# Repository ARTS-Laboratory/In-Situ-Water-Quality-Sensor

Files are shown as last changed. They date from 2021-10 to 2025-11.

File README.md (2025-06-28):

# In-Situ-Water-Quality-Sensor
An in situ water quality sensor for monitoring water quality from a UAV-deployable sensor package. The sensor packages provide real-time monitoring of pH, conductivity, temperature, and turbidity. 

<p align="center">
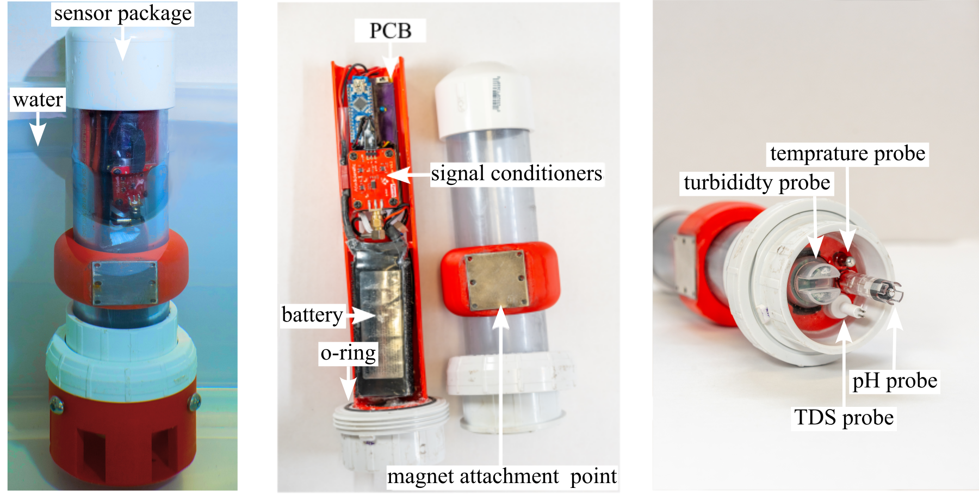
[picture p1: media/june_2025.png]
 <br> 
UAV deployment mechanism as of June 2025.
</p>

<p align="center">
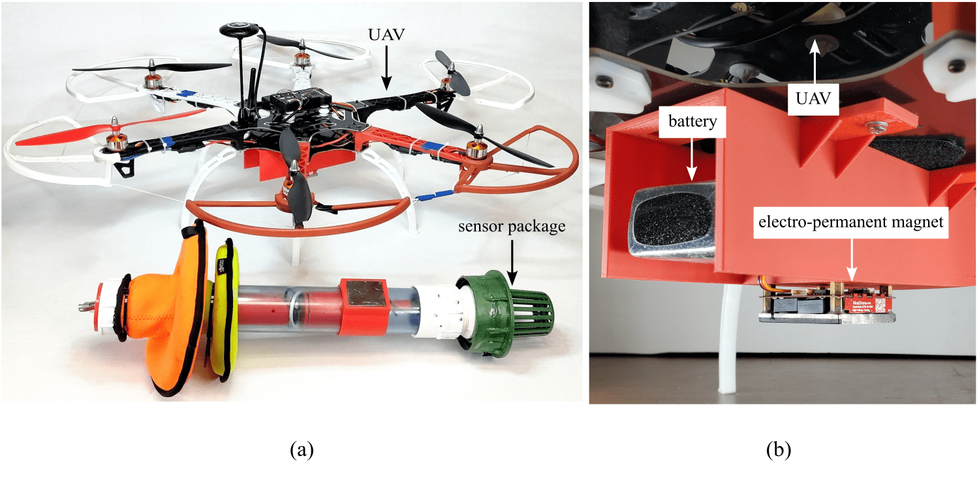
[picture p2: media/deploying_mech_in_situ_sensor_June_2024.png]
 <br> 
UAV deployment mechanism as of June 2024.
</p>

<p align="center">
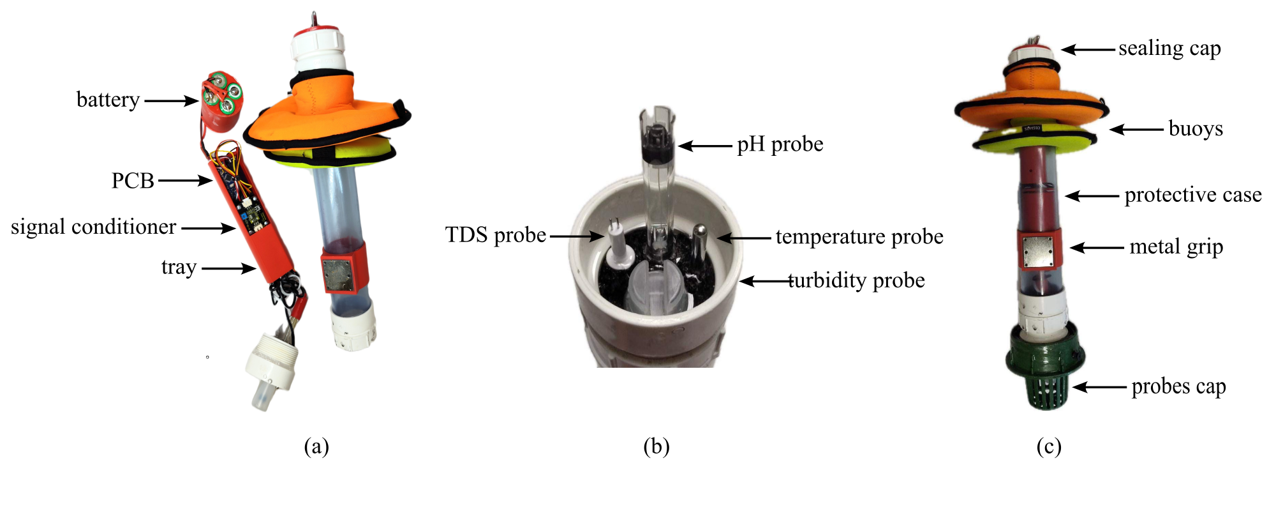
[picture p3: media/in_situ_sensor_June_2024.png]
 <br> 
System configuration as of June 2024 used for testing UAV deployments. 
</p>

<p align="center">
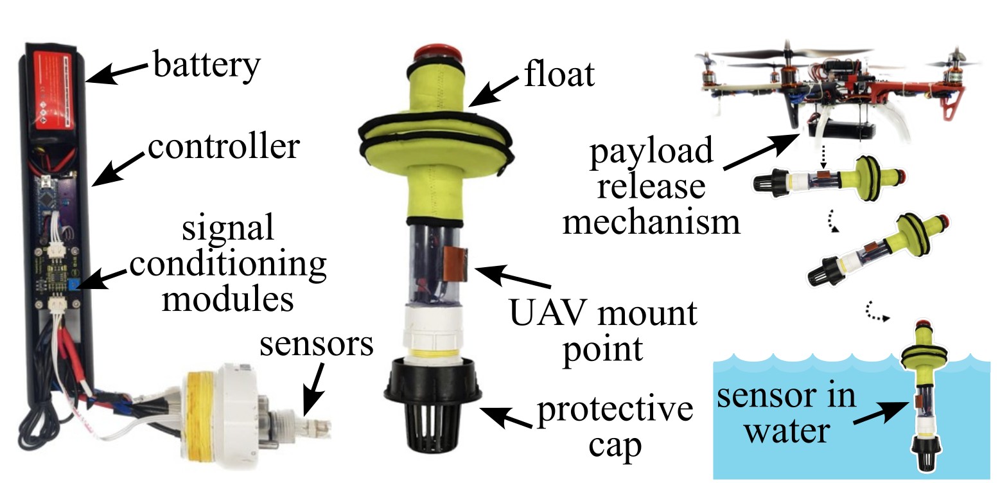
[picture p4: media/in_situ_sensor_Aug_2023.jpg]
 <br> 
System configuration as of August 2023 used for testing UAV deployments. 
</p>

<p align="center">
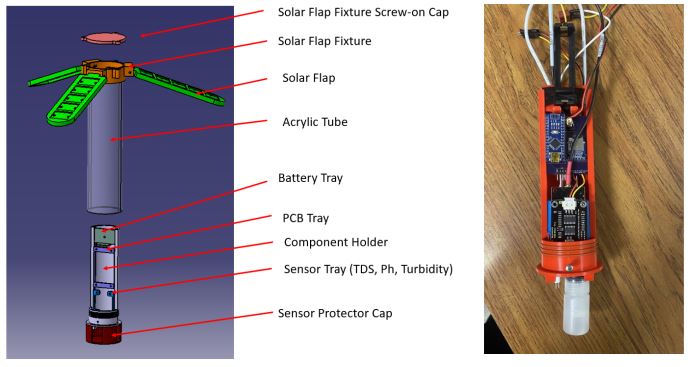
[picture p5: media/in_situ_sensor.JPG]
 <br> 
An early configuration of the proposed UAV-deployable in situ water quality system with pedal-style solar panels. 
</p>

## [System Design](system_design)
The system (hardware and software) design for the project.

## Licensing and Citation

This work is licensed under a Creative Commons Attribution-ShareAlike 4.0 International License [cc-by-sa 4.0].



Cite this data as: 

#### Bibtex

@Misc{ARTSLabSituWaterQuality,    
  author = {{ARTS-L}ab},  
  howpublished = {GitHub},  
  title  = {In-Situ-Water-Quality-Sensor},  
  groups = {ARTS-Lab},    
  url    = {https://github.com/ARTS-Laboratory/In-Situ-Water-Quality-Sensor},   
}

<p align="center">
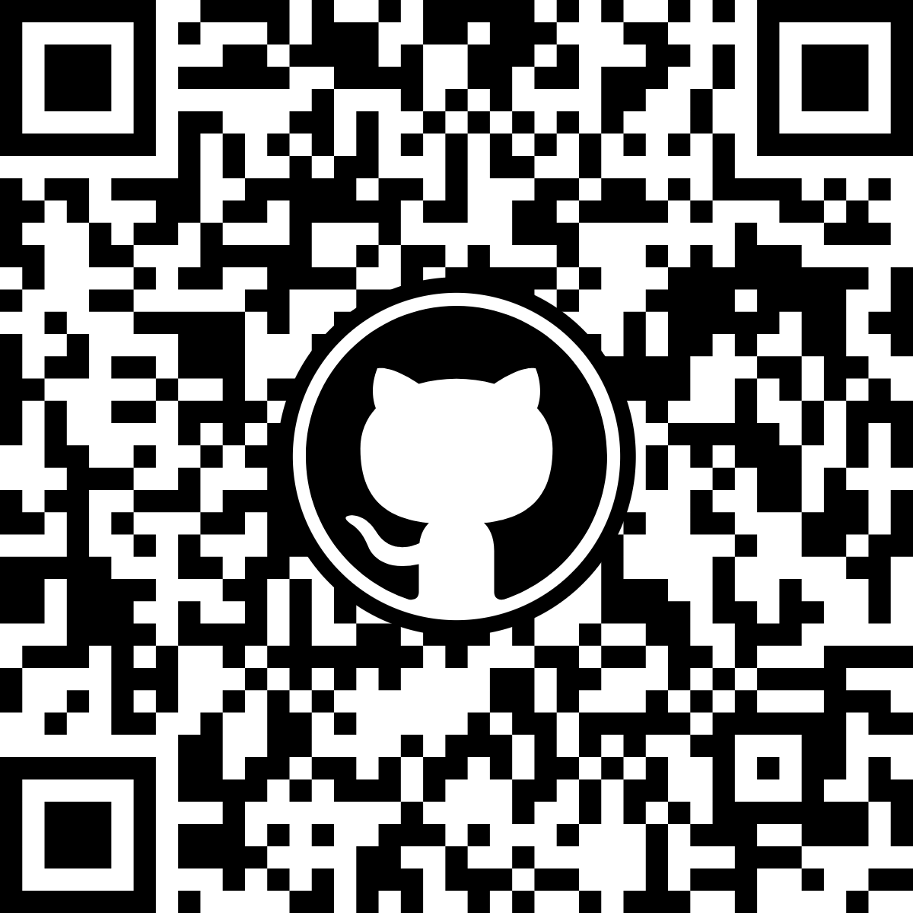
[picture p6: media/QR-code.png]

</p>
<p align="center">
QR code for repo.

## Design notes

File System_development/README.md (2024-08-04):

# Sensor Package Variations  
Sensor package variations are named after freshwater lakes in South Carolina. 

## Jocassee
* Sensor package designed for data acquisition with onboard data storage and wireless data transmission. 

## Marion 
* Sensor package designed with edge AI capabilities.

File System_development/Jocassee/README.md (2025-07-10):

# Jocassee
An in situ water quality sensor for monitoring water quality

## V0.1
1. Measures pH and turbidity 
1. Saves data to SD card
1. Water-tight case 
1. This is a general dump of all the initial files. 

## V0.2
1. This is just a clean-up version of 0.1. 
1. The pads on the 1026 resistors are too small
1. move the SMA connection over.
1. Need to add a ground plane to V0.3.
1. Need to add the SMA footprint on V0.3.

## V0.3
1. New designs for PCB boards. 

## V 0.4.0
1. Includes part designs necessary to assemble the water sensor package.
2. Missing probe protector.
3. Missing Apple air tag mount.
4. Need to adjust hold positioning for Solar Flap Fixture.

## V 0.4.5 
1. Includes 2 component holders. One for TDS and pH, and another for TDS, pH, and Turbidity.
2. Includes a probe protector that prevents damage to the ends of the probes.
3. Updated solar flaps to house solar flaps wired in parallel
4. Solar Flap Fixture Cap updated to include a spot for Apple air tag
5. Updated Solar Flap Fixture. (position for holes moved, height extended, and inside tabs reduced from 4 to 2)
6. Need to make these parts out of solid plastic pieces and leak-test the package.
7. PCB Design includes RTC Module and Micro SD Card Module.
8. The PCB includes Footprints for the PH, TDS, and Turbidity Sensors.
9. Updated Arduino code to Measure the PH, TDS, and Turbidity of the water.
10. The code controls the sampling time and saves the collected data on a micro SD card.

## V 0.4.6 
1. These are general updates and a major reorganization of all the files in V0.4.5.
2. The updated PCB design includes footprints pH, Turbidity, TDS, and Temperature sensors.
3. The Updated Arduino code.
4. The Kriging Code

## V 0.4.7
1. The updated PCB design includes footprints for a GPS Module
2. Updated Arduino Code to include GPS readings
3. Added multiple designs for 3D printed Buoys
5. Added a design for a cap that includes a spot to attach an antenna
6. Included STL files and G-code for each buoy and cap.
7. Added an assembly to better size 3D printed parts for the Chassis
8. Added a Bill of Matirials

## V 0.5.0
### Version of Refrence for "UAV-Deployable Sensor Nodes for Spatial and Temporal In-Situ Water Quality Monitoring and Mapping", Burnett et al. 2025
 1. Minor changes to chassis to more densly pack the sensors
 2. Minor Buoy/drop mechanism design revisions
 3. Minor changes to PCB mounting screw holes
sensor_package_2025

## V 0.5.1
### Usability upgrades on V 0.5.0
    
## V 0.6.0
1. Updated PCB design including GPS, wireless module and latest compact signal conditioning boards for pH & TDS sensing.
2. Includes an easily dettachable solar buoy for increased operational endurance.
3. Includes waterproof connector for solar power input and battery charging from external sources.
4. Contains a BMS for effecient battery charging and load sharing.
5. Features a capless design where O'ring is used to seal the top opening.
6. Includes step files for every components used in sensor node.

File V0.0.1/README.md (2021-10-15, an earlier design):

# V1

## Case design
1. Three o-rings
1. 3D printed end caps
1. PCV case
1. Solar Wing
1. Turbidity Case
1. Solar Connection

## PCB Design
1. pH sensor on mezzanine board 
1. Real-time clock on PCB
1. MicroSD adaptor for data collection
1. Battery slot for powering the PCB
1. CR1025 battery for Real-time clock
1. Rails for connecting to the turbidty PCB

## Code
1. Records data
1. Calibration done on the micro-controller.

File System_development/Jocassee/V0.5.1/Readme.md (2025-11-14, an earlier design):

## Instructions for the In-Situ Water Quality Sensor Deployment and Recovery <br>

### Deployment- <br>

* Upload the code and monitor the sensor readings. 

* Insert the SD card. 

* Rename the CSV file according to the sensor package number within the arduino IDE. 

* Turn the switch off. 

* Install the battery. 

* Turn the switch on. 

* Check the red signal on the board. 

* Assemble the outer case and the sensor package, put grease on the O-ring. 

* Remove the pH probe cover Tape the inside of the bottom protective red cover. 

* Mount the bottom cover. 

### Recovery- 

* Rinse the entire sensor package with tap water and wipe it dry. 

* Remove the bottom cover. 

* Rinse the sensor probes with filtered or distilled water, sepcially the pH probe. 

* Separate the outer case from the sensor package. 

* Turn the switch off. 

* Reattach the storage solution tube to the pH probe and store it properly. 

* Remove the battery. 

* Remove the SD card. 

* Check the recorded data. 

### Note: pH probe storage solution needs to be changed every 2 storage cycles.

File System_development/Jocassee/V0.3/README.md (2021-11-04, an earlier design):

# V1

## Case design
1. Three o-rings
1. 3D printed end caps
1. PCV case
1. Solar Wing
1. Turbidity Case
1. Solar Connection

## PCB Design
1. pH sensor reverse engineered onto mezzanine board
1. Real-time clock on PCB
1. MicroSD adapter for data collection
1. Battery slot for powering the PCB
1. CR1025 battery for Real-time clock
1. Rails for connecting to the turbidity PCB

## Code
1. Records data
1. Calibration done on the micro-controller.

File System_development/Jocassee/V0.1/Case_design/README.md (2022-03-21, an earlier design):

# Case Design

## file #1
1. ...

## file #2
1. ...

## file #3
1. ...

## file #4
1. ...

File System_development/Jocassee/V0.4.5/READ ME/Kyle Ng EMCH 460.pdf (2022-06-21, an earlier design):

# WATER SENSOR PACKAGE

## Kyle Ng

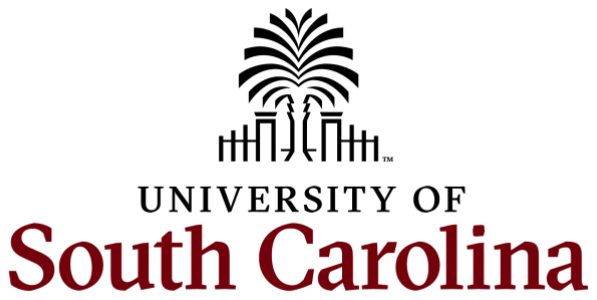
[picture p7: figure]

# PLAN FOR ENVIRONMENTAL SENSOR PACKAGE

## 1. Create a datalogger for TDS sensor 2. Combine all the sensors into one datalogger 3. Design PCB to tie everything together 4. Design waterproof case to house all components 5. Test and validate

1/18/2022

## - Need to order TDS Probe and obtain a SD card and SD card reader - RTC, SD card reader, and TDS sensor code

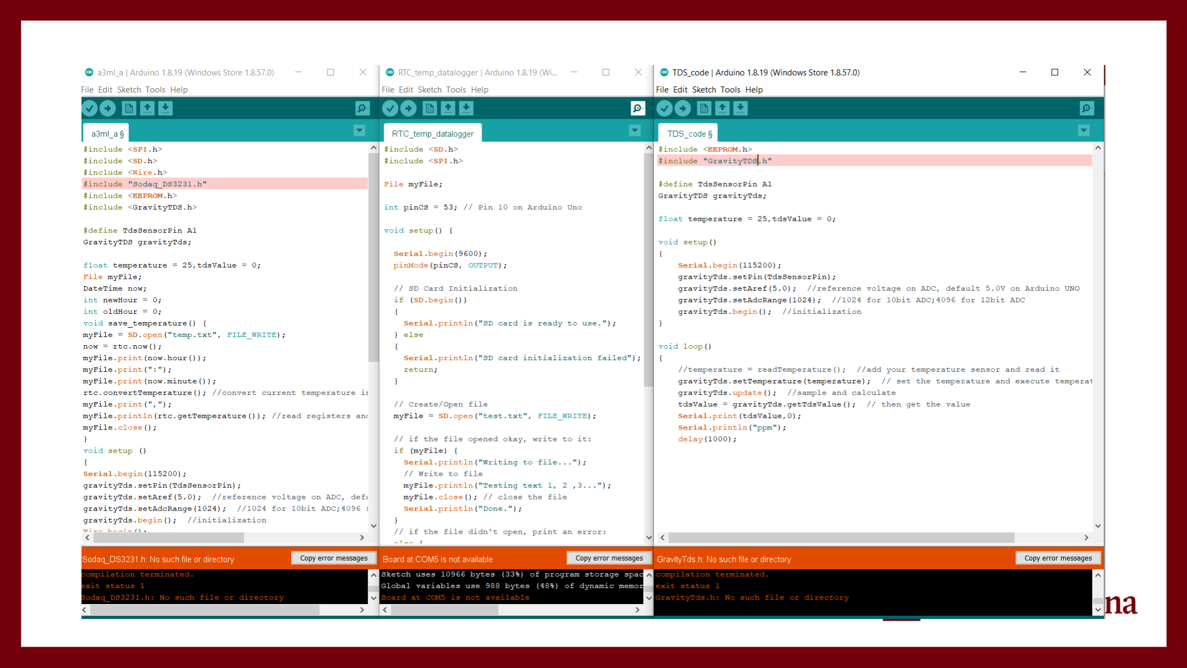
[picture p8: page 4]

1/25/2022

## - Code for TDS sensor data logging to SD card working - Need to test code when probe arrives

2/1/2022

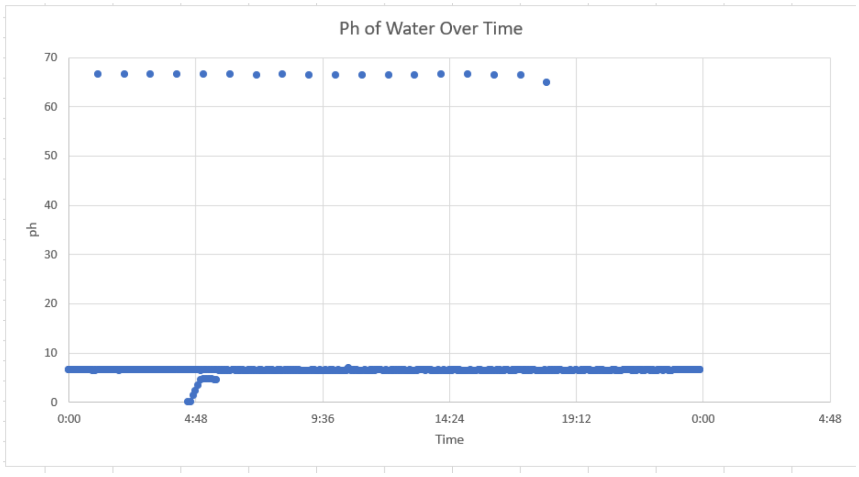
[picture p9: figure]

## Turbidity

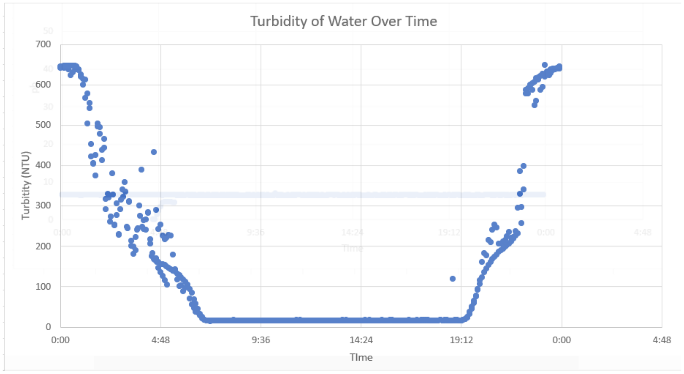
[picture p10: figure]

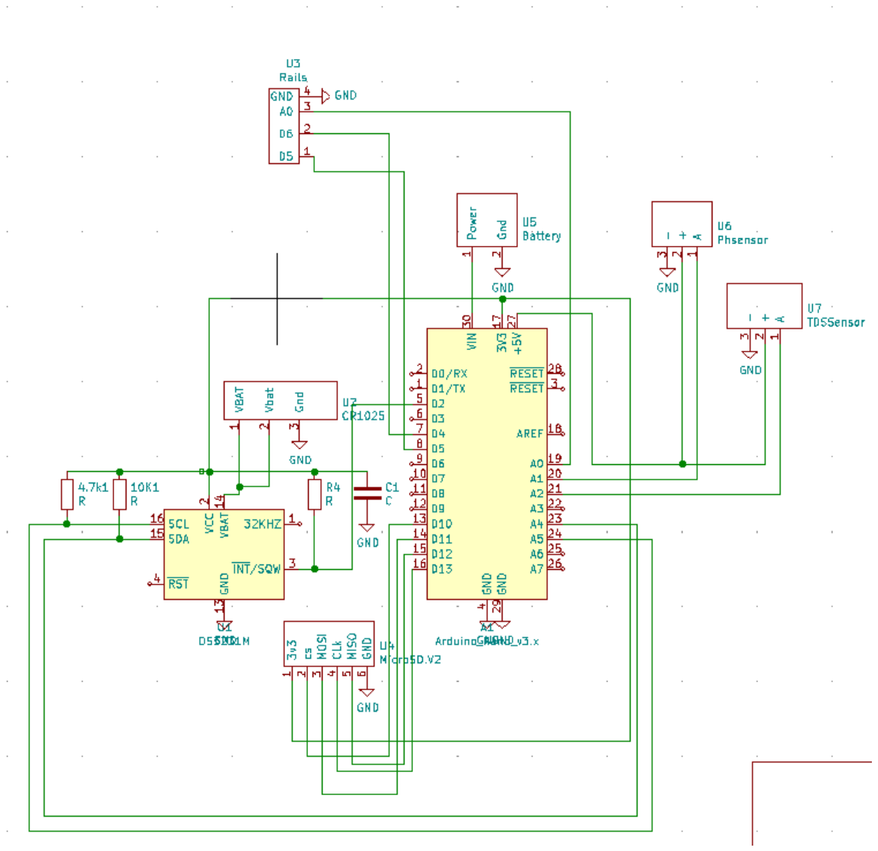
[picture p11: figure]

2/15/2022

- Included TDS sensor into current sensor package
- Next Step: rearrange
components on board to fit in new housing

# HOUSING FOR SENSORS

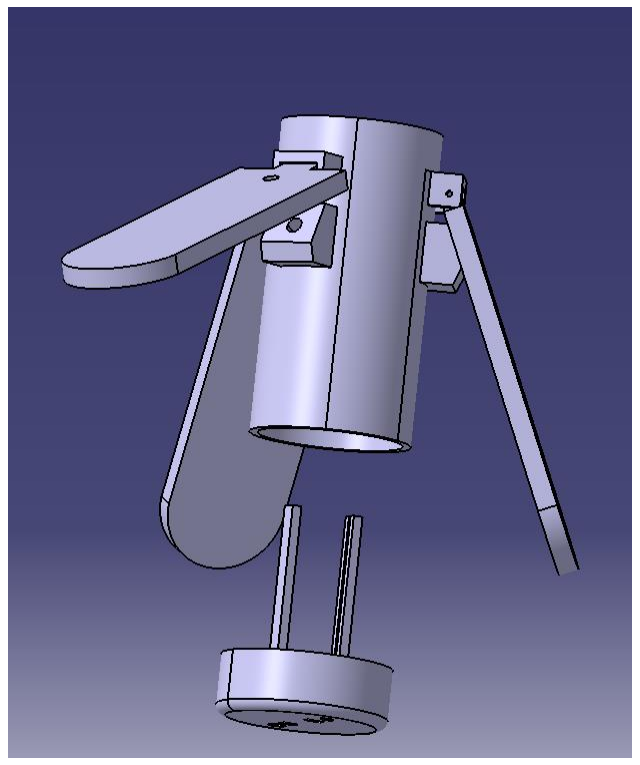
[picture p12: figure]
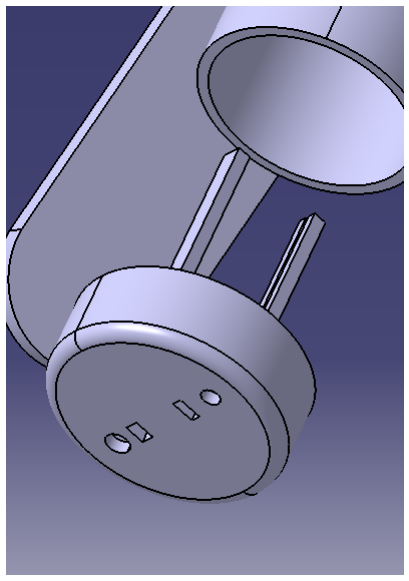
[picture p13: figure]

- Solar flaps can be used as a tripod
- Probes and sensors will fit through the bottom
- PCB with components will fit between the slots in the two rails
- Next Steps:
- Add protection for
probes/sensors on the
bottom
- Add battery holder to
the bottom component
holder

2/22/2022

- Solar Charging Findings
- TDS Testing
- Updated Housing for components

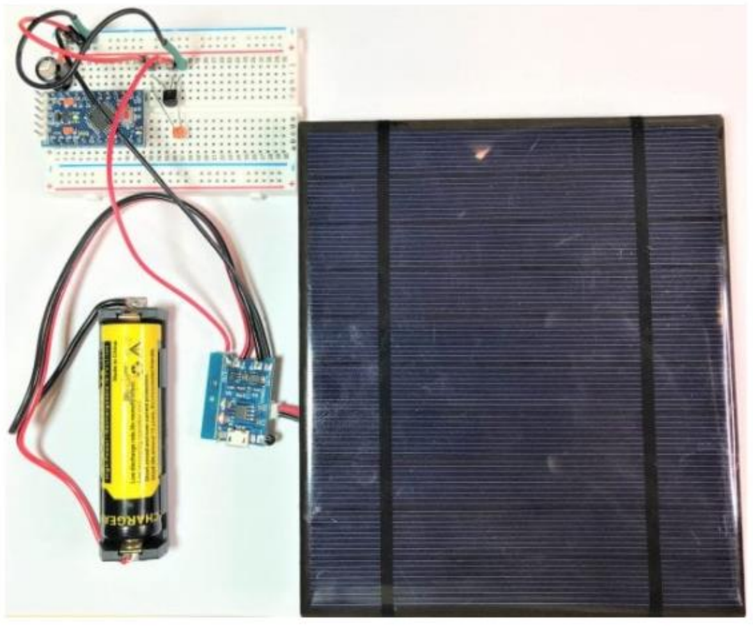
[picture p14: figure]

# SOLAR CHARGING

- Arduino Pro-Mini, (https://www.amazon.com/gp/product/B01981EBBA?creative=9325&creativeASIN=B01981EBBA&linkId=bea0be0a28fa56cb6d4992cf304c7f2b) or Arduino Nano (https://www.amazon.com/Arduino-A000005-ARDUINO-Nano/dp/B0097AU5OU?linkId=a3b7d3a0dcc652364ddb8e8986edb0be&language=en_US)
- TP4056 battery charge controller (https://www.amazon.com/Makerfocus-Charging-Lithium-Battery-Protection/dp/B071RG4YWM?linkId=957634db00eebaef6169a13464f34088&language=en_US)
- 100 uF capacitor
- 100 nF capacitor (https://www.amazon.com/gp/product/B01MSQOX0Q?creative=9325&creativeASIN=B01MSQOX0Q&linkId=4faf7291a2b537642b4fe23a8e3a5942)
- MCP1700-3302E 3.3V voltage regulator (https://www.amazon.com/MICROCHIP-TECHNOLOGY-MCP1700-3302E-Positive-Regulator/dp/B00M1E0FVM?linkId=d0bcd6895ad98490119027404b917f5a&language=en_US)
- 3.7V 18650 Lithium Ion battery (2000 mAH or more)* (https://www.amazon.com/Kastar-Replacement-GMB-B117-Stabilizer-Feiyu-Tech/dp/B08RN6N52C?linkId=bbe94ebc36754c41b8562e7bd0be650b&language=en_US)
- 6V DC, 500 mA solar panel* (https://www.amazon.com/Sunnytech-583ma-Module-System-Charger/dp/B00HQY56KM?linkId=d1df4e3088d10c13b16e6950e386a366&language=en_US)
- Breadboard (https://www.amazon.com/gp/product/B07DL13RZH?creative=9325&creativeASIN=B07DL13RZH&linkId=ffac51d787abb539fe6e475bb1a7395a)
- Jumper wires (https://www.amazon.com/gp/product/B07GD2PGY4?creative=9325&creativeASIN=B07GD2PGY4&linkId=830b215653e24d7801a496770987b18d)

# SOLAR CHARGING CONFIGURATION

- Charges battery

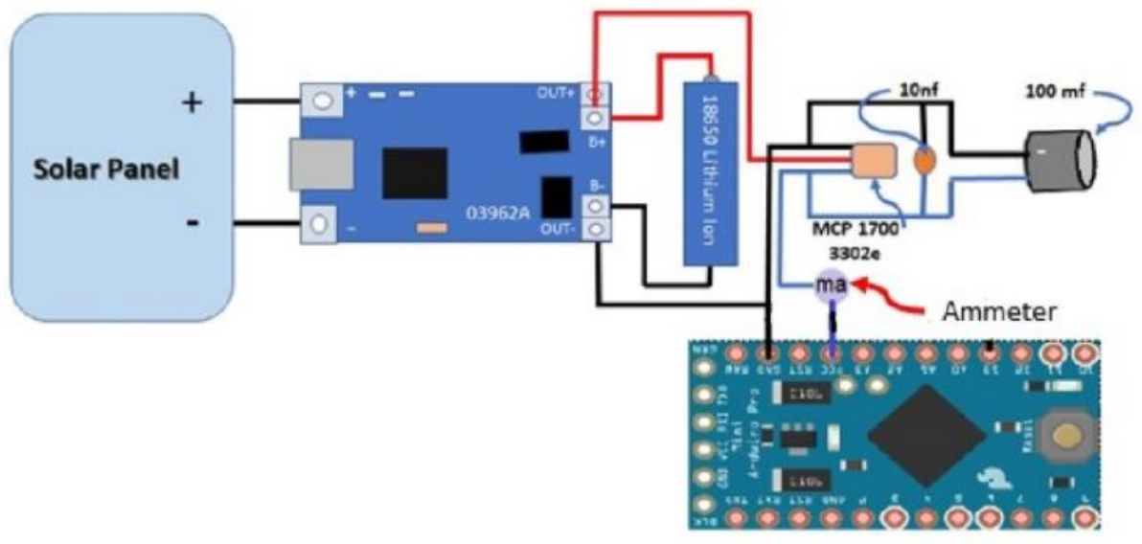
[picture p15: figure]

- Supplies power to circuit when solar is producing enough energy
- Charge circuit disconnects at night and the battery takes over as power source
- Lithium-Ion batteries can be connected in parallel if both batteries are identical

# MODEL UPDATES

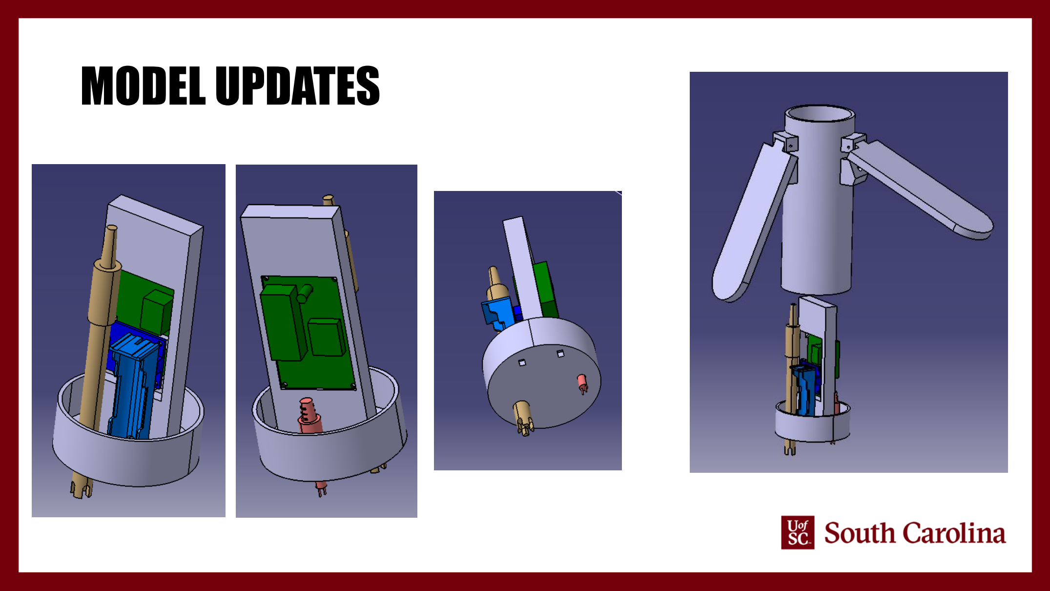
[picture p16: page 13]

# TDS SALT EXPERIMENT

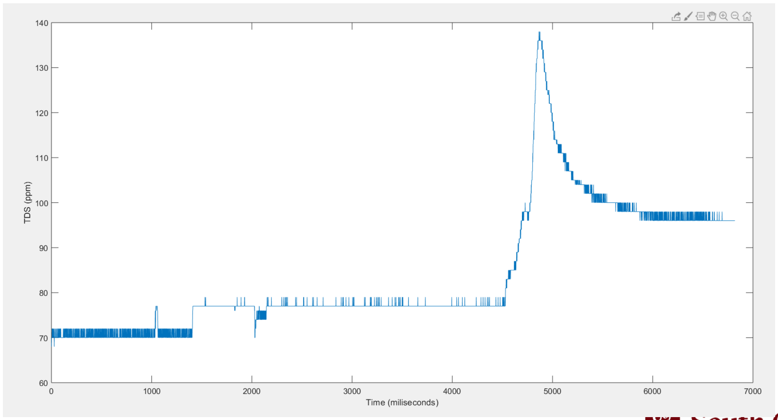
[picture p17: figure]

# UPDATED COMPONENT TRAY

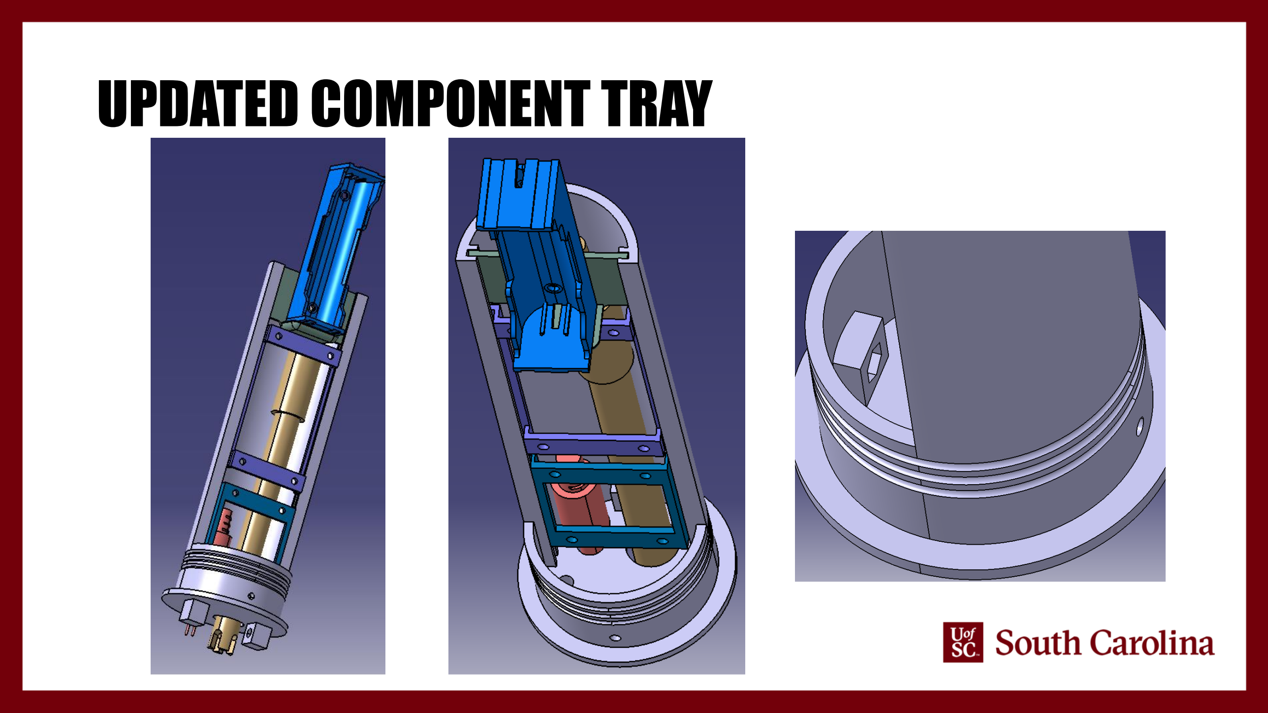
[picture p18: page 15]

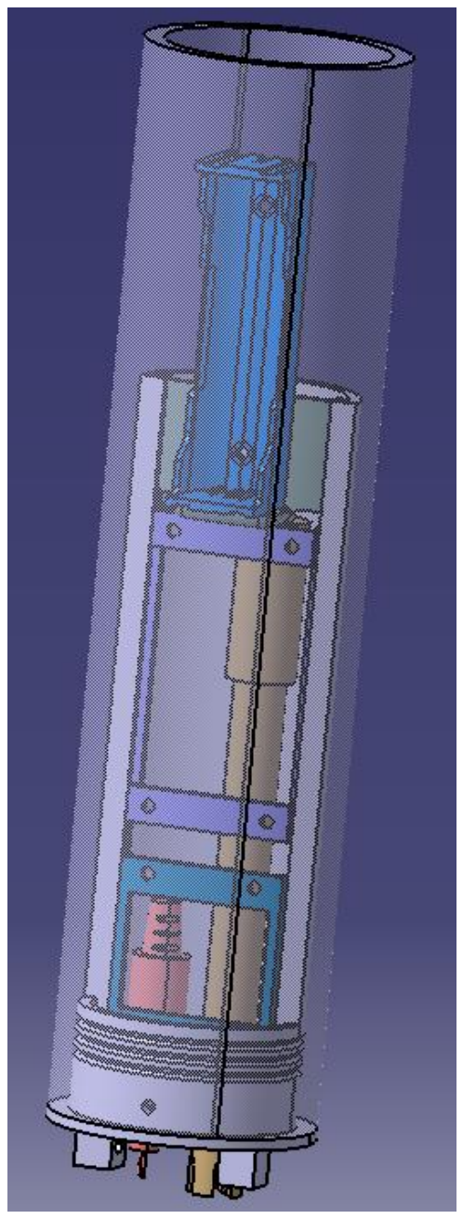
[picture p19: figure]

3/15/2022

## Updates:

### - Redesigned component holder - Redesigned water proof solar panel petal holder and cap - Test fit components in the component holder - Collected parts for solar charging

## Goals:

### - Create initial standalone solar battery charger

# SOLAR PANEL HOLDER AND TOP CAP

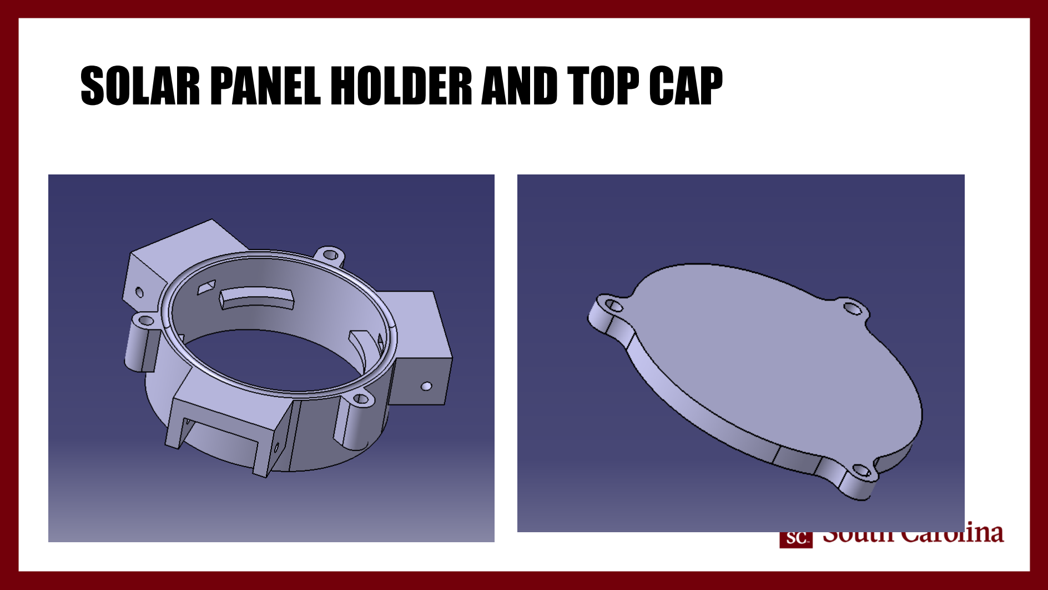
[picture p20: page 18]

# ASSEMBLY

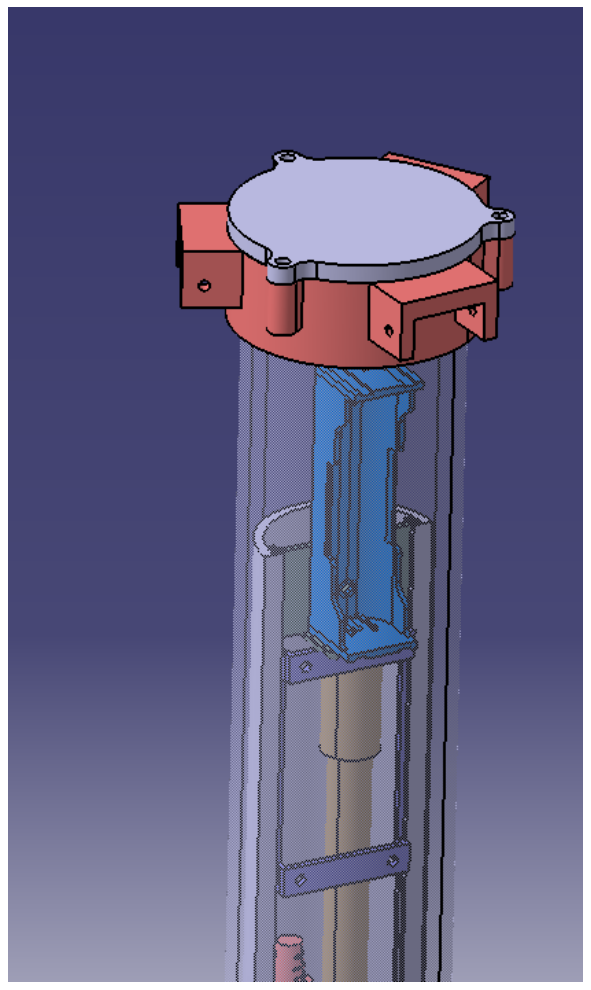
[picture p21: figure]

# 3/29/2022 SOLAR UPDATE

- Current and voltage reading from solar panel
- Current and voltage reading from solar panel with voltage step down
- Current and voltage reading from solar panel with voltage step down and bms
- Reviewing Daniels design

# SOLAR PANELS

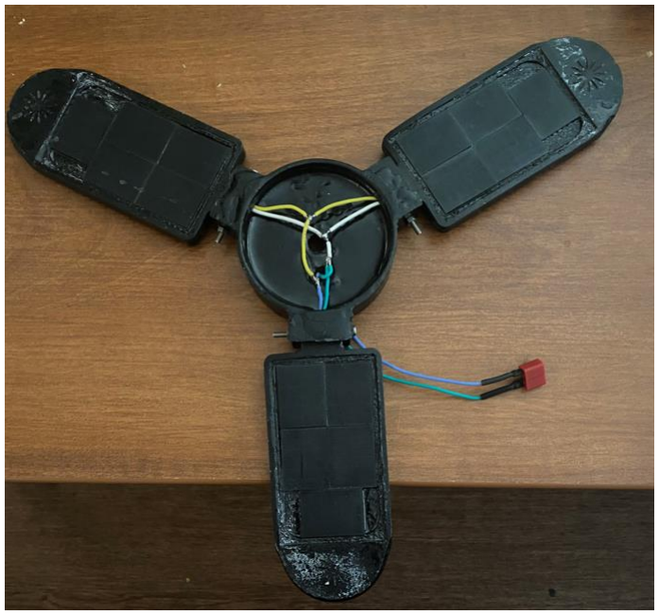
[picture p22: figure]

## - Voltage : 16V - Current : 40mA

# SOLAR PANELS WITH VOLTAGE STEP DOWN

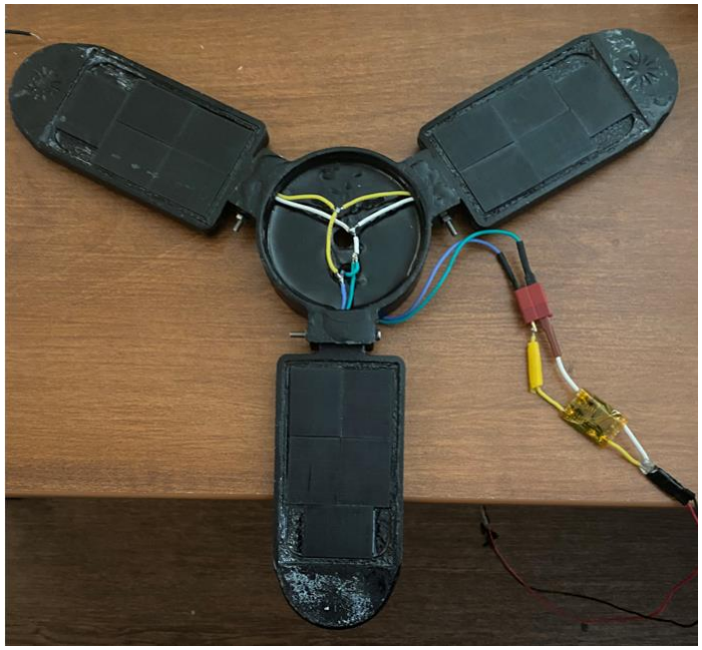
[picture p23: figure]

## - Voltage : 5V - Current : 160mA

# SOLAR PANELS WITH VOLTAGE STEP DOWN AND BMS

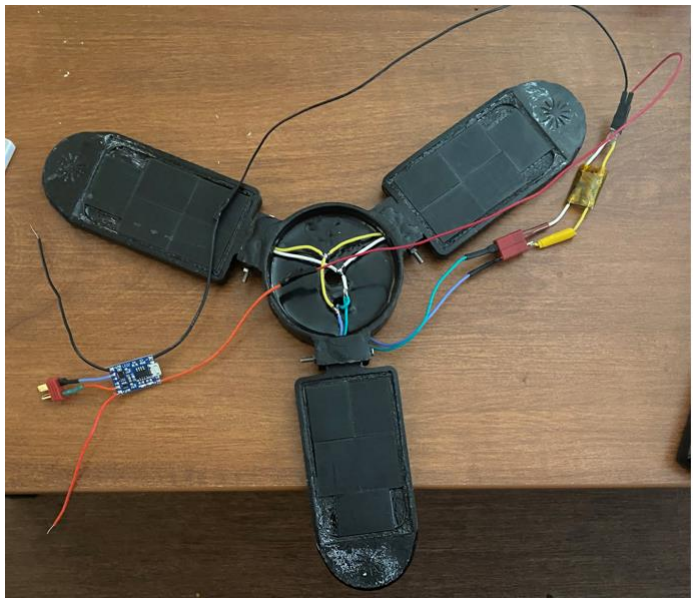
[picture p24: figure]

## - Voltage : 4.2V - Current : 33mA

# WIRING FOR PANELS

+

+

+

+

+

# INDIVIDUAL SOLAR CELL INFORMATION

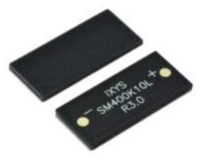
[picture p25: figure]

Individual Cells Specs
- Power : 132.3mW
- Voltage : 8.29 V
- Current : 21 mA

18 cells in parallel
- Voltage : 8.29V
- Current : 378mA

Battery Specs

Would need 42 cells to achieve standard charge rate

4/5/2022

## New updates

- Removed solar panels from epoxy to resolder and test
- Pulled information on package power consumption

## Future plans

- Run test on fully charged 18650 to set a baseline for how long it will sustain the package for
- Run test with solar charging added to see the impact it has on battery life
- Design a probe protector for the bottom of the package
- Create probe mounting cap out of PVC
- Waterproof the 3D printed solar panel flap holder or make it out of solid plastic as well
- Make the cap to the solar flap holder out of metal

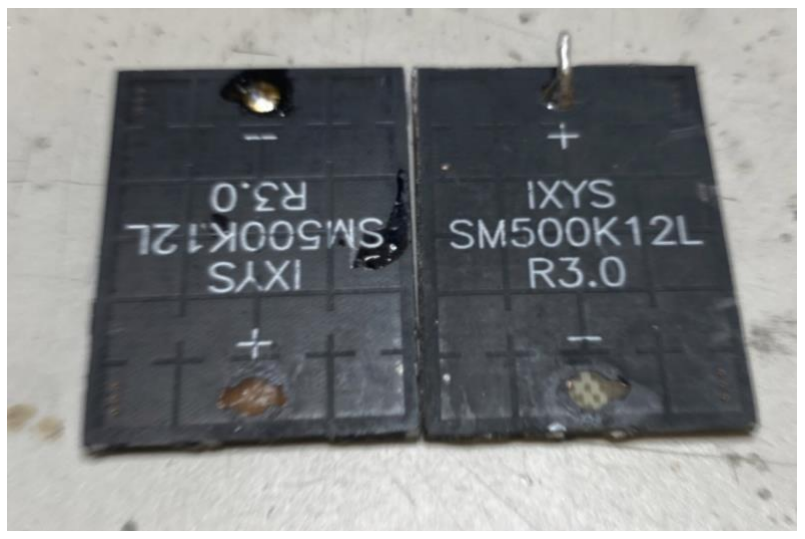
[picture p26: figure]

# SOLAR CELLS

- 2 cells were damaged while removing from epoxy and cannot be used
- The remaining cells were wired in parallel and produce 7.4V and 157mA
- Arudino nano power consumption: 19mA
- TDS power consumption: 3 – 6mA
- Ph power consumption: 3 mA

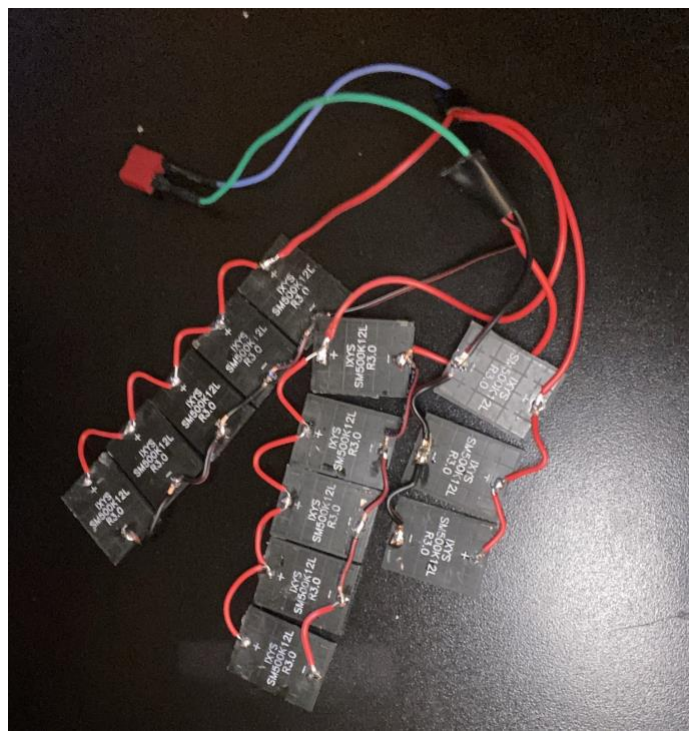
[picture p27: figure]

4/12/2022

## New updates

- Solar charging circuit has been soldered together with connectors

## Future plans

- Run test on fully charged 18650 to set a baseline for how long it will sustain the package for
- Run test with solar charging added to see the impact it has on battery life
- Design a probe protector for the bottom of the package
- Create probe mounting cap out of PVC
- Waterproof the 3D printed solar panel flap holder or make it out of solid plastic as well
- Add metal piece to the solar cap for magnet
- Add in Air tag holder to solar cap
- Redesign solar flap for new solar panel arrangment

# THANKS!

Name
Title
Email
Social

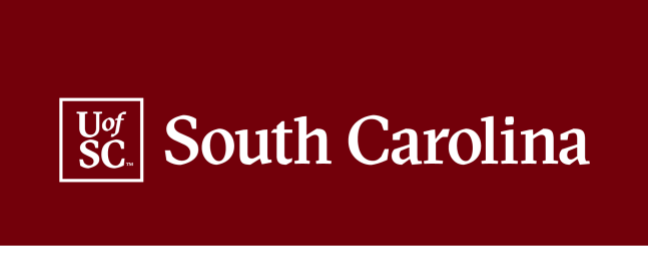
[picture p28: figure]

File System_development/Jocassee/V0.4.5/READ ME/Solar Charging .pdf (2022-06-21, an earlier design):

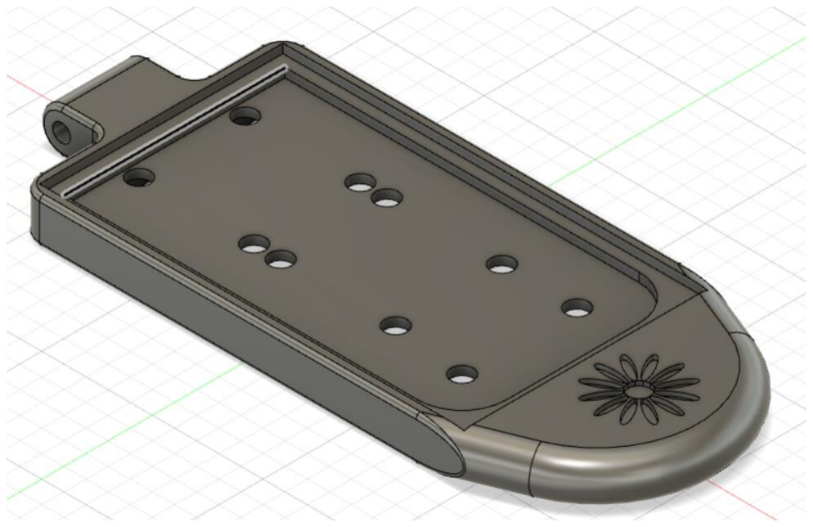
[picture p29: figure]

## SENSOR PACKAGE DESIGN

- Solar Petal
- Will hold 5 solar cells that will produce 16 volts.
- 3 of these items.
- Round end to take force from water.
- Going to have the wires and cells enclosed.

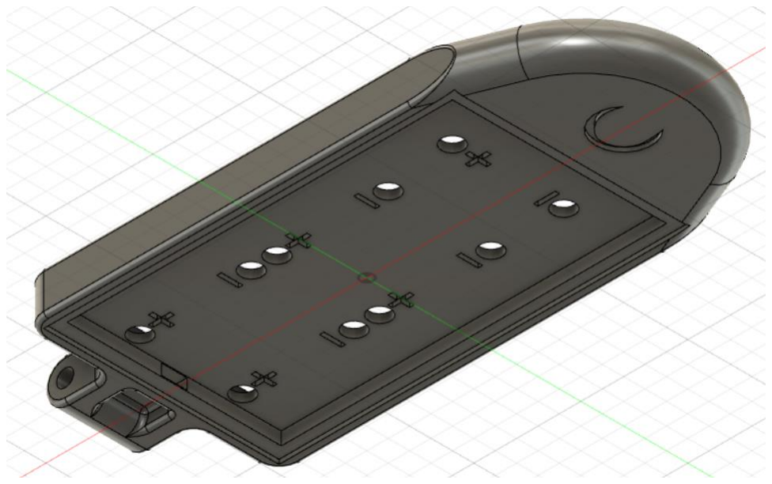
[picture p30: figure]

SOLAR CELLS CONT.


- More solar cells were added to the design.
- Volts: 25 volts

## SOLAR CELLS


- Soldered together solar cell in parallel and series.
- Volts: 16 V
- Amps: 7.9 milliamps.


SOLAR CELLS UPDATE

- Solar cells have been given DC stepdown.
- To decrease voltage and
increase amperage.
- The battery and solar cells both have DC step-down.
- Voltage: 5V.
- Amps: 15 milliamps.

SENSOR PACKAGE DESIGN CONT.


- Solar connecter
- Will connect all solar petals to the sensor package.
- Will have metal top for the magnets.
- A DC stepdown to drop the voltage from 16 to around 5-6 Volts.
- Current 15 milliamps.

## BATTERY CHARGER


- Will be connected to the solar cells.
- The diode is used to prevent voltage backlash.
- Will charge a battery from the solar cells.

## BATTERY CHARGING SYSTEM

- https://www.circuitbasics.com/how-to-use-solar-panels-topower-the-arduino/


## SCHEMATIC


## YOUTUBE VIDEO EXAMPLE PROJECT

- https://www.youtube.com/watch?v=37kGva3NW8w

## SETUP FOR MORE BATTERIES


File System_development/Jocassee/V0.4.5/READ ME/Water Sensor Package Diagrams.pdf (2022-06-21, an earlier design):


## Solar Flap Fixture Screw-on Cap

## Solar Flap Fixture

## Solar Flap

## Acrylic Tube

## Battery Tray

## PCB Tray

## Sensor Tray (TDS, Ph, Turbidity)

## Sensor Protector Cap

- There are prongs under the Solar Flap Fixture Screw-on Cap that will hold an apple air tag
- Use threaded inserts for the solar flap to screw on the screw-on cap
- There are holes in the Solar Flap Fixture that wires for solar charging can be fed into. Glue/epoxy will need to added to fill in gaps after wires are in.
- Solar cells will be epoxied into the solar flap when the charging setup has been tested and verified
- Sensor probes will go in first and will fit behind the electrical components (refer to next slide)
- Internal components will mount to Battery Tray, PCB Tray, and Sensor Tray. Once these are situated, glue can be used to keep trays from sliding up and down.
- Sensor protector cap will be glued on last. (will need to fit grommets and turbidity before gluing it on.
- There are holes in the bottom of the component holder that nuts can go into. Push them in until they line up with holes in the side of the component holder
- Holes will be drilled into the side of the acrylic tube to line up with the component holder so that screws can be screwed into the nuts that were installed. This is what will keep the component holder from sliding out of the acrylic tube
- Most of these components will need to be made out of PVC and not 3D printed for water proofing
- Clear coat seems to cause PLA to warp
- Epoxy might work, but it is hard to apply evenly and thoroughly

## Component Holder

# Relevant Pictures


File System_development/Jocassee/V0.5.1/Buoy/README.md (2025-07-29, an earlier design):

# An overview of the different buoy design types
Withen the OldVersions folder are designs that are incompatible with eyebolts

Among these designs are clamshell-style designs and sphere-style designs. Below is an example:

<p align="center">
 <br> 
</p>

There are three different design types withen the eyebolt compatible folder.

The first such design type is a clamshell style design, with a roof:

<p align="center">
 <br> 
</p>

The second design type is a clamshell style design, without a roof:

<p align="center">
 <br> 
</p>

The third design type consists of non-clamshell style designs:

<p align="center">
 <br> 
</p>

The fourth design type is a clamshell design that is not compatible with an eyebolt, and should be anchored with a rope tied around the buoy itself. These designs are found in the rope direct folder. Below is an example:

<p align="center">
 <br> 
</p>

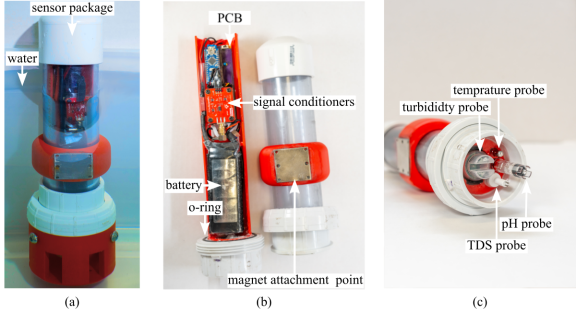
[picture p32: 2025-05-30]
in_situ_sensor_June_2025.png

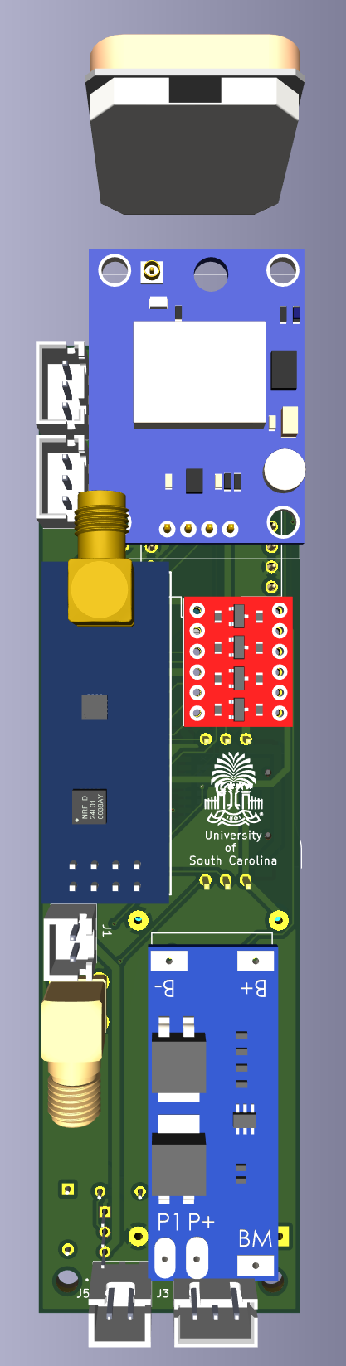
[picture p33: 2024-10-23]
System_development/Jocassee/V0.6.0/EDA/V0.6.3/Images/PCB BOTTOM.PNG

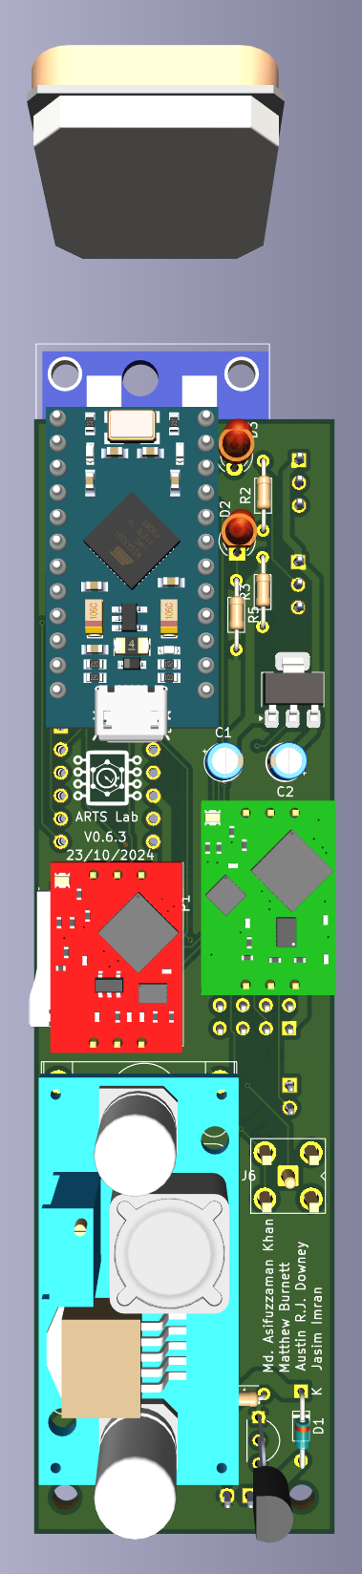
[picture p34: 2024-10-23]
System_development/Jocassee/V0.6.0/EDA/V0.6.3/Images/PCB TOP.PNG

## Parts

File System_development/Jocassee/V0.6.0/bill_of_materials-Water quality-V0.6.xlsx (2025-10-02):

Designator | Component | Amount | Individual Cost | Total Cost | Vendor 1 | Vendor 2 | Vendor 3 | Vendor 4 | Vendor 5 | Vendor 6
Arduino Nano | Arduino Nano | 1 | $25.70 | $25.70 | https://store-usa.arduino.cc/products/arduino-nano?gad_source=1 | https://www.digikey.com/en/products/detail/arduino/A000005/2638989?gclsrc=aw.ds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 | https://www.ebay.com/itm/254630577493?chn=ps&google_free_listing_action=view_item&gQT=2
PVC union | 2 in x 2 in Fitting Pipe Size, Schedule 40, Female Female, White, Union | 1 | $15.77 | $15.77 | https://www.grainger.com/product/22FL17?RIID=51819294775&GID=729415832&mid=OrderConfirmation_REST&gucid=EMT:11126144:Item:CSM-323&emcid=NA:Item
Schedule 40 clear PVC | PVC, Excelon, 2 in Nominal Pipe Size, 8 ft Overall Lg | 1 | $60.76 | $60.76 | https://www.grainger.com/product/1AAZ8?gclsrc=aw.ds&gad_source=1&gad_campaignid=21375667808
O-rings | O-Ring: Buna-N, Round, 2 mm C.S., 35 mm I.D., 10 PK | 1 | $2.68 | $2.68
 |  |  |  | $0.00
 |  |  |  | $0.00
 |  |  |  | $0.00
 |  |  |  | $0.00
 |  |  |  | $0.00
 |  |  |  | $0.00
 |  |  |  | $0.00
 |  |  |  | $0.00
 |  |  |  | $0.00
 |  |  | Total | $104.91
 |  |  | Total Cost | $209.82

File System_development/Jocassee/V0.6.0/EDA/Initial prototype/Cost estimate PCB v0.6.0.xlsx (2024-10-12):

Item | Quantity | Price per unit (USD) | Net price (USD) | Comments
PCB (Min qty 3, ref: oshpark) | 1 | 6.5 | 6.5 | single unit cost considered
PH module (https://atlas-scientific.com/embedded-solutions/ezo-ph-circuit/) | 1 | 50 | 50
PH probe (https://atlas-scientific.com/probes/consumer-grade-ph-probe/) | 1 | 50 | 50
TDS Module (https://atlas-scientific.com/embedded-solutions/ezo-conductivity-circuit/) | 1 | 68 | 68
TDS probe (https://www.amazon.com/Yuly-Dissolved-Analysis-Water-quality-Monitoring/dp/B0CS9M2H26) | 1 | 4 | 4 | Atlas confirmed that this probe will work with the TDS module
Turbidity sensor (https://www.mouser.com/ProductDetail/Amphenol-Advanced-Sensors/TSD-10?qs=cmBPKiaX3MylKvR%252BTrNAhw%3D%3D) | 1 | 7 | 7
Temp (https://www.amazon.com/DS18B20-Temperature-Waterproof-Digital-Thermal/dp/B09SWMJM6R) | 1 | 2 | 2
Arduino Pro micro (https://www.amazon.com/AITRIP-ATmega32U4-Compatible-Leonardo-ATmega328/dp/B08BJTS2N8) | 1 | 10 | 10
5v Buck converter (https://www.amazon.com/Module-Universal-Adjustable-Voltage-Converter/dp/B07KNTVNCC) | 1 | 1.76 | 1.76
3.3v Level shifter (https://www.adafruit.com/product/1787) | 1 | 1.5 | 1.5
3.3 V regulator (https://www.amazon.com/Regulator-Positive-Maximum-SOT-223-4-CJT1117B-3-3/dp/B0CSMKNRKM) | 1 | 0.6 | 0.6 | single unit cost considered
SD card slot (https://www.amazon.com/connectors-1415mm-Tablet-Vehicle-Navigation/dp/B093LBK96T) | 1 | 0.66 | 0.66 | single unit cost considered
Neo M8N GPS (https://www.amazon.com/GY-GPSV3-NEO-M8N-Module-Controller-1-65-3-6V/dp/B0D97XG978) | 1 | 14.07 | 14.07
NRF24L01 (https://www.amazon.com/NRF24L01-2-4G-DIY-Board-Module/dp/B0B2TXZWW3) | 1 | 1.8 | 1.8
XH2.54 - 2 Pin (https://www.amazon.com/XH2-54-Connector-Terminal-Housing-XH2-54-2P/dp/B09PK21FXR) | 1 | 0.48 | 0.48 | single unit cost considered
XH2.54 - 3 Pin (https://www.amazon.com/Connector-Terminal-Housing-XH2-54-3P-Electronic/dp/B09PK21V82) | 1 | 0.5 | 0.5 | single unit cost considered
 |  | Total | 218.87
Price excluded: BNC connector, solar cells, capacitors, nRF24 external antenna, filament cost,

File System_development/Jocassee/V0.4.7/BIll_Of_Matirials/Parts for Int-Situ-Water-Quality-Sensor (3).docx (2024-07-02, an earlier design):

All Container Parts

Item (# of parts) (Grainger Part Number)

- PVC Female Adaptor (1) (1WJY4)
- Epoxy
- 3” Round Atrium Grate (1) (Home Depot)
- ABS Male Adaptor (1) (1WJD3)
- 1.5” by 1.5” steel plate (1) (We have steel)
- 14” long 2” diameter PVC Pipe (1) (788VR8 for 10ft white, 1AAZ8 for 8ft clear)
- ½” long ¼” diameter nut and bolt (2) (we have)
- 2” diameter O-ring (2) (2KAE2 is a 25 pack)
- Battery and PCB board tray 3D print (1)
- Steel plate holder 3D print (1)
- Buoy 3D Print (1)
- Spray Foam door and window
- PVC Glue (We have)

All Electronics

- Analog to digital converting PCB board (3)
- Custom PCB board (1)
- Arduino Mini (1)
- ¼” long screws (8)
- ½”Screw connectors (4)
- White rectangular 3 prong snap-in female wire connector (3)
- Black rectangular 3 prong female wire connector (3)
- pH sensor (1) (16Y953)
- Thermometer (1)
- Water particle sensor (electric) (1)
- Water particle sensor (light) (1) (https://www.newark.com/amphenol-advanced-sensors/tsd-10/turbidity-sensor-5vdc-phototransistor/dp/18X9859?gad_source=1&CMP=KNC-GUSA-GEN-PMAX-Shopping-New)
- GPS Module (1)

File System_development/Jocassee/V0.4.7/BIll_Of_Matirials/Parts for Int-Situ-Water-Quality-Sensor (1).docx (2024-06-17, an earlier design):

All Container Parts

- Black Zip Ties (2)
- Part 31-1241 2” Charlotte pvc (1)
- Danco 86809 Slip Joint Nut and Washer PVC, white (1) ((only need Nut)
- Part 33401 Oatey (1)
- Epoxy
- 3” Round Atrium Grate, Green (1)
- Part 31-638 White(PVC) Charlotte (1)
- Part 12 2” PVC Charlotte (1)
- 1.5” by 1.5” steel plate
- Clear 14” long 2” diameter PVC Pipe (1)
- ½” long ¼” diameter nut and bolt (2)
- Battery and PCB board tray 3D print (1)
- Steel plate holder 3D print (1)
- Buoy 3D Print (1)
- Spray Foam

All Electronics

- Analog to digital converting PCB board (3)
- Custom PCB board (1)
- Arduino Mini (1)
- ¼” long screws (8)
- ½”Screw connectors (4)
- White rectangular 3 prong snap-in female wire connector (3)
- Black rectangular 3 prong female wire connector (3)
- pH sensor (1)
- Thermometer (1)
- Water particle sensor (electric) (1)
- Water particle sensor (light) (1)
- GPS Module (1)

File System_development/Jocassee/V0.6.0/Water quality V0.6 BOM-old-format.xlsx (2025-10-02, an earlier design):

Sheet: Electronics BOM
PCB Reference | Component | Qty | Unit cost (USD) | Net cost (USD) | Source
C1,C2 | Polarized Capacitor (https://www.digikey.com/en/products/detail/cornell-dubilier-knowles/SEK220M025ST/1627140) | 2 | 0.59 | 1.18 | digikey
D1 | Schottky Diode (https://www.digikey.my/en/products/detail/vishay-general-semiconductor-diodes-division/1N5817-E3-54/1023529) | 1 | 0.31 | 0.31 | digikey
D3 | 3mm LED red (https://www.digikey.com/en/products/detail/w%C3%BCrth-elektronik/151033RS03000/4490003) | 1 | 0.18 | 0.18 | digikey
D2 | 3mm LED green (https://www.digikey.com/en/products/detail/w%C3%BCrth-elektronik/151033GS03000/4490000) | 1 | 0.26 | 0.26 | digikey
J2,J3,J4 | 3pin XH2.54 male connector (https://www.digikey.com/en/products/detail/jst-sales-america-inc/B3B-XH-A/1651046) | 3 | 0.19 | 0.57 | digikey
J1,J5 | 2pin XH2.54 male connector (https://www.digikey.com/en/products/detail/jst-sales-america-inc/B2B-XH-A/1651045) | 2 | 0.14 | 0.28 | digikey
J6 | SMA connector for pH probe (https://www.digikey.com/en/products/detail/te-connectivity-linx/CONSMA002-G/5012144) | 1 | 4.85 | 4.85 | digikey
M8N_GPS1 | Ublox_Neo_M8N_GPS (https://www.ebay.com/itm/266897100593?_skw=NEO-M8N+GPS&itmmeta=01JC4ZKC372D7B26E93187JSA8) | 1 | 12.74 | 12.74 | eBay
P1 | SD card socket (https://www.digikey.com/en/products/detail/attend-technology/112J-TDAR-R01/17634680) | 1 | 2.54 | 2.54 | digikey
Q1 | 2N2222A/BC337 BJT or equivalent (https://www.digikey.com/en/products/detail/gearbox-labs/PART-TRANSISTOR-2N2222/16159943) | 1 | 0.22 | 0.22 | digikey
R1 | 1K ohm resistor (https://www.digikey.com/en/products/detail/stackpole-electronics-inc/RNF14FTD1K00/1706678) | 1 | 0.1 | 0.1 | digikey
R2,R4 | 4.7K ohm resistor (https://www.digikey.com/en/products/detail/stackpole-electronics-inc/CF18JT4K70/1741708) | 2 | 0.1 | 0.2 | digikey
R3 | 470 ohm resistor (https://www.digikey.com/en/products/detail/stackpole-electronics-inc/CF14JT470R/1741440) | 1 | 0.1 | 0.1 | digikey
R5,R6 | 160/220 ohm resistor (https://www.digikey.com/en/products/detail/stackpole-electronics-inc/CF14JT160R/1741302) | 2 | 0.1 | 0.2 | digikey
R7,R8 | 100K ohm resistor (https://www.digikey.com/en/products/detail/stackpole-electronics-inc/CF14JT100K/1741263) | 2 | 0.1 | 0.2 | digikey
U1 | NRF24L01+PA+LNA (https://www.ebay.com/itm/266790757067?_skw=nrf24l01+pa+lna&itmmeta=01JBYRV06QPYB0N21D6RTKG1BJ&var=566533004074) | 1 | 2.5 | 2.5 | eBay
U2 | Arduino ProMicro (https://www.digikey.com/en/products/detail/sparkfun-electronics/DEV-12640/5140825) | 1 | 19.5 | 19.5 | digikey
U3 | EZO_PH circuit (https://atlas-scientific.com/embedded-solutions/ezo-ph-circuit/) | 1 | 45.99 | 45.99 | atlas
U4 | EZO_TDS circuit (https://atlas-scientific.com/embedded-solutions/ezo-conductivity-circuit/) | 1 | 67.99 | 67.99 | atlas
U5 | DC-DC Stepdown converter LM2596 (https://www.ebay.com/itm/124221762232?_skw=LM2596+DC-DC&itmmeta=01JC4ZR9NBV9A4KA41KNF8FB6X) | 1 | 1.85 | 1.85 | eBay
U6 | HX-2S-JH10 BMS (https://www.ebay.com/itm/122175451692?_skw=2s+7.4v+bms&itmmeta=01JC4ZYQC0WA4Q7FSXJ13Q3MD7) | 1 | 2.15 | 2.15 | eBay
U7 | BOB-12009, 5V to 3.3V level shifter (https://www.digikey.com/en/products/detail/sparkfun-electronics/BOB-12009/5673795) | 1 | 3.5 | 3.5 | digikey
U8 | AMS1117 3.3v regulator SOT-223-3L (https://www.digikey.com/en/products/detail/umw/AMS1117-3-3/17635254) | 1 | 0.63 | 0.63 | digikey
N/A | SMA female to male extension cable (https://www.ebay.com/itm/141363729667?_skw=SMA+Male+to+SMA+Female&itmmeta=01JBYSFVCGRGZ7V7YWN5SNYH25&var=440506777313) | 1 | 8.28 | 8.28 | eBay
N/A | 2s Lipo battery 7.4V (87 x 33 x 20 mm) (https://www.ebay.com/itm/385936313712?_skw=ZEEE+2s+2200mah&itmmeta=01JC503SS3GJ6DT520MX0DKGZ0) | 1 | 11.7 | 11.7 | eBay
N/A | Waterproof JST Connector (https://www.ebay.com/itm/296294957822?itmmeta=01JBYSTER2HRK2QQS40HWZGCEW&var=594321428484) | 2 | 2.58 | 5.16 | eBay
N/A | Solar panels (https://www.digikey.com/en/products/detail/anysolar-ltd/SM141K06TF/14311398) | 9 | 7.39 | 66.51 | digikey
 |  |  | Total | 259.69
Some nice to have items but not mandatory
 | 40 pin Female header connector 2.54mm (https://www.digikey.com/en/products/detail/chip-quik-inc/HDR100IMP40F-G-V-TH/5978200) | 1 | 1.09 | 1.09 | digikey
 | 40 pin Male header connector 2.54mm (https://www.digikey.com/en/products/detail/chip-quik-inc/HDR-ETD/5978263) | 1 | 1.59 | 1.59 | digikey
 | USB to serial converter module (https://www.ebay.com/itm/225911345316?_skw=USB+to+serial+conerter+module&itmmeta=01JBYSWZSCW24XB1T7ZAXWS544&var=525000706225) | 1 | 2.75 | 2.75 | eBay
 |  |  | Total | 5.43

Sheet: Fixture BOM
Component | Qty | Unit cost (USD) | Net cost (USD) | Source
PVC union (https://www.grainger.com/product/22FL17?RIID=51819294775&GID=729415832&mid=OrderConfirmation_REST&gucid=EMT:11126144:Item:CSM-323&emcid=NA:Item) | 1 | 19.55 | 19.55 | Grainger
Schedule 40 clear PVC (https://www.grainger.com/product/1AAZ8?RIID=51819294775&GID=729415832&mid=OrderConfirmation_REST&gucid=EMT:11126144:Item:CSM-323&emcid=NA:Item) | 1 ft | 7.9 | 7.9 | Grainger
O-rings (https://www.grainger.com/product/O-Ring-Buna-N-41KW27) | 1 | 0.26 | 0.26 | Grainger
 |  | Total | 27.71

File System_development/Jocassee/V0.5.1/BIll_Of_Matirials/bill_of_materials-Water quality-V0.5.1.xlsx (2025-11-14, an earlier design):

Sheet: Electronics BOM
PCB Reference | Component spec / part number | Qty | Unit cost (USD) | Net cost (USD) | Vendor 1 | Vendor 2 | Vendor 3
C1 0.1uF | Capacitor_SMD:C_1206_3216Metric_Pad1.33x1.80mm_HandSolder | 1 | 0.11 | 0.11 | https://www.digikey.com/en/products/detail/nextgen-components/1206B104K500BD/15776047
U3 | SWITCH OS102011MS2QN1 | 1 | 0.71 | 0.71 | https://www.digikey.com/en/products/detail/c-k/OS102011MS2QN1/411602 | https://www.mouser.com/ProductDetail/CK/OS102011MS2QN1?qs=WtljUlYws5RvQ1hEv876nQ%3D%3D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 | https://www.jameco.com/z/OS102011MS2QN1-C-K-Slide-Switch-SPDT-ON-ON-100mA-12VDC-Through-Hole-5-08mm-Pitch_2313927.html
D1 | LED 3.0mm | 1 | 0.16 | 0.16 | https://www.digikey.com/en/products/detail/w%C3%BCrth-elektronik/151033RS03000/4490003
U2 | SD card module | 1 | 1.69 | 1.69 | https://www.ebay.com/itm/203852249807?_skw=SD+card+module+mini&itmmeta=01JWS7YRSNYRE9JPQ1403XF1SB
A1 | Arduino Nano | 1 | 3.67 | 3.67 | https://www.ebay.com/itm/283932038203?_skw=arduino+nano&itmmeta=01JWS81PY2BK5W7AA2FK7T4DBS
U6 | DS3231M+ | 1 | 10.98 | 10.98 | https://www.digikey.com/en/products/detail/analog-devices-inc-maxim-integrated/DS3231M-TRL/2402421 | https://www.mouser.com/ProductDetail/Analog-Devices-Maxim-Integrated/DS3231M+TRL?qs=Bakm8ERcljq5PBzSwLfmgg%3D%3D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
BT1 | Coin cell Battery Holder BK-870 | 1 | 0.58 | 0.58 | https://www.digikey.com/en/products/detail/mpd-memory-protection-devices/BK-870/3829737
U8 | 3pin XH2.54 male connector (https://www.digikey.com/en/products/detail/jst-sales-america-inc/B3B-XH-A/1651046) | 1 | 0.13 | 0.13 | https://www.digikey.com/en/products/detail/jst-sales-america-inc/B3B-XH-A/1651046
R2 470ohm | Resistor_SMD:R_1206_3216Metric_Pad1.30x1.75mm_HandSolder | 1 | 0.1 | 0.1 | https://www.digikey.com/en/products/detail/bourns-inc/CR1206-JW-471ELF/3741054
R1 4.7K | Resistor_SMD:R_1206_3216Metric_Pad1.30x1.75mm_HandSolder | 1 | 0.1 | 0.1 | https://www.digikey.com/en/products/detail/bourns-inc/CR1206-JW-472ELF/3785627
N/A | Coin cell battery CR-1025-ND | 1 | 1.09 | 1.09 | https://www.digikey.com/en/products/detail/jauch-quartz/CR1025/16399048
N/A | 11.1V 3000mAH Lipo battery with T connector | 1 | 46.72 | 46.72 | https://us.ovonicshop.com/products/ovonic-50c-11-1v-3000mah-3s1p-deans-2pcs?_pos=7&_sid=207a99678&_ss=r | https://www.ebay.com/itm/184508325888?chn=ps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 | https://www.motionrc.com/products/admiral-3300mah-3s-11-1v-30c-lipo-battery-with-t-connector-epr33003?variant=19047011142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
N/A | Atlas pH conditioning circuit | 1 | 26.11 | 26.11 | https://www.digikey.com/en/products/detail/atlas-scientific/SRV-PH/16003016?gad_source=1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
N/A | Turbidity conditioning circuit and sensor | 1 | 9.9 | 9.9 | https://www.digikey.com/en/products/detail/dfrobot/SEN0189/6588606?gad_source=1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 | https://www.keyestudio.com/products/keyestudio-turbidity-sensor-v10-with-wires-compatible-with-arduino-for-water-testing
N/A | pH probe ENV 30 | 1 | 49.99 | 49.99 | https://www.digikey.com/en/products/detail/atlas-scientific/ENV-30-PH/16003028?gad_source=1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 | https://atlas-scientific.com/probes/consumer-grade-ph-probe/
N/A | TDS probe and conditioning circuit | 1 | 19.95 | 19.95 | https://www.ebay.com/itm/184291373846?chn=ps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 | https://www.keyestudio.com/products/keyestudio-tds-meter-v10-board-module-water-meter-filter-measuring-water-quality-for-arduino-unor3
N/A | ds18b20 temperature sensor | 1 | 2.55 | 2.55 | https://www.ebay.com/itm/224193475936?_skw=ds18b20&itmmeta=01JWS9436Y9FERAQTKDM3HA2HJ | https://www.dfrobot.com/product-689.html?gad_source=1&gad_campaignid=22388643497&gbraid=0AAAAADucPlAUqBsu3pP_X85ogWbbBBgBa
N/A | Male T connector for lipo | 1 | 1.25 | 1.25 | https://www.digikey.com/en/products/detail/sparkfun-electronics/11864/6818769?gad_source=1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 | https://rcbattery.com/deans-style-t-connector-plug-male-side-5pcs-bag.html?gad_source=1&gad_campaignid=12748770885&gbraid=0AAAAACRJLSYkFmISdyi2KqVyCMKzbiA4R
N/A | 15 pin female header 2.54 mm | 2 | 2.2 | 4.4 | https://www.digikey.com/en/products/detail/samtec-inc/SSW-115-01-F-S/7879494?gad_source=1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
N/A | PCB | 1 | 8 | 8 | https://oshpark.com/
N/A | Rope | 1 | 9.47 | 9.47 | https://www.grainger.com/product/General-Purpose-Utility-Rope-20TL72 | https://www.mscdirect.com/product/details/17155631 | https://www.harborfreight.com/18-in-x-50-ft-paracord-56740.html
N/A | pH protective pouch | 1 | 5.8 | 5.8 | https://www.testequipmentdepot.com/ohaus-30064800-replacement-ph-sensor-protect-bottle-10-in-bag.html | https://selectumllc.com/i/ohaus-30064800?s=ads&gad_source=1&gad_campaignid=23117909187&gbraid=0AAAAApptgRbBnKHiWLgv_Xj-PtCTaUYZH | https://www.dscbalances.com/products/ph-sensor-protect-bottle-10-in-bag
N/A | pH storage solution | 1 | 38 | 38 | https://www.grainger.com/product/OAKTON-Electrode-Storage-Solution-9MD19 | https://www.digikey.com/en/products/detail/atlas-scientific/CHEM-PH-S/16003006?gclsrc=aw.ds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 (https://www.dscbalances.com/products/ph-sensor-protect-bottle-10-in-bag) | https://atlas-scientific.com/calibration-solutions/ph-storage-solution/ (https://www.digikey.com/en/products/detail/atlas-scientific/CHEM-PH-S/16003006?gclsrc=aw.ds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)
 |  |  | Total | 241.35

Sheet: Fixture BOM
Component | Qty per sensor | Unit price (USD) | Net price (USD) | vendor 1 | vendor 2 | vendor 3
PVC union | 1 | 19.56 | 19.56 | https://www.grainger.com/product/22FL17?RIID=51819294775&GID=729415832 | https://www.homedepot.com/pep/Apollo-2-in-x-2-in-PVC-Slip-Joint-x-Slip-Joint-Union-PVCU2/317901067?locale=en-US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
Schedule 40 clear PVC pipe | 10 inches | 69.69 | 7.26 | https://www.grainger.com/product/1AAZ8?gclsrc=aw.ds&gad_source=1&gad_campaignid=21375667808
Schedule 40 socket cap | 1 | 1.47 | 1.47 | https://www.grainger.com/product/22FJ37?RIID=51819294775&GID=729415832 | https://www.homedepot.com/pep/Charlotte-Pipe-2-in-PVC-Socket-Schedule-40-Pressure-Cap-PVC021161600HD/203811678?locale=en-US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 | https://www.homedepot.com/pep/Charlotte-Pipe-2-in-OD-PVC-Test-Cap-Fitting-PVC-00132-0800HD/203947220?locale=en-US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
M3 standoofs 8mm | 12 | 1.13 | 13.56 | https://www.digikey.com/en/products/detail/w%C3%BCrth-elektronik/971080365/9488753 | https://www.ebay.com/itm/326491279997
M3 standoffs 6mm | 4 | 0.85 | 3.4 | https://www.digikey.com/en/products/detail/w%C3%BCrth-elektronik/971060365/9488747 | https://www.ebay.com/itm/295005028017
M3 nylon hex nut | 4 | 0.13 | 0.52 | https://www.digikey.com/en/products/detail/keystone-electronics/4688/4499297?gad_source=1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 | https://www.grainger.com/product/Hex-Nut-M3-0-50-Thread-4AGJ9?opr=ODOH
2 part clear epoxy | 1 pack | 47.86 | 47.86 | https://www.grainger.com/product/25F529?gad_source=1&gad_campaignid=21369464154&gclsrc=aw.ds | https://www.ebay.com/itm/365353922077?itmmeta=01JZNA1PV76QEB7T5CVVGGADC6 | https://www.grainger.com/product/PC-PRODUCTS-Epoxy-Adhesive-PC-11-4AUV9?opr=ODOH&analytics=FM:Order%20History
 |  |  | 93.63

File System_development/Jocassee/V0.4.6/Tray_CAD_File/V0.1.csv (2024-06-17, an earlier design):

Reference | Value | Datasheet | Footprint | Qty | DNP | # | Description
A1 | Arduino_Nano_v3.x | http://www.mouser.com/pdfdocs/Gravitech_Arduino_Nano3_0.pdf | Module:Arduino_Nano | 1 |  | 1
BT1 | Battery_Cell | ~ | WATER_SENSOR:battery_holder_10mm | 1 |  | 2
C1 | C | ~ | Capacitor_SMD:C_1206_3216Metric_Pad1.33x1.80mm_HandSolder | 1 |  | 3
D1 | LED | ~ | LED_THT:LED_D3.0mm | 1 |  | 4
R1,R2 | R | ~ | Resistor_SMD:R_1206_3216Metric_Pad1.30x1.75mm_HandSolder | 2 |  | 5
U1 | water_Battery |  | WATER_SENSOR:Battery_Input | 1 |  | 6
U2 | SD |  | WATER_SENSOR:SD | 1 |  | 7
U3 | switch |  | WATER_SENSOR:grounded_switch | 1 |  | 8
U4,U5,U7 | Sensor |  | -- mixed values -- | 3 |  | 9
U6 | DS3231M | http://datasheets.maximintegrated.com/en/ds/DS3231.pdf | Package_SO:SOIC-16W_7.5x10.3mm_P1.27mm | 1 |  | 10
U8 | Temp |  | WATER_SENSOR:Temp. | 1 |  | 11

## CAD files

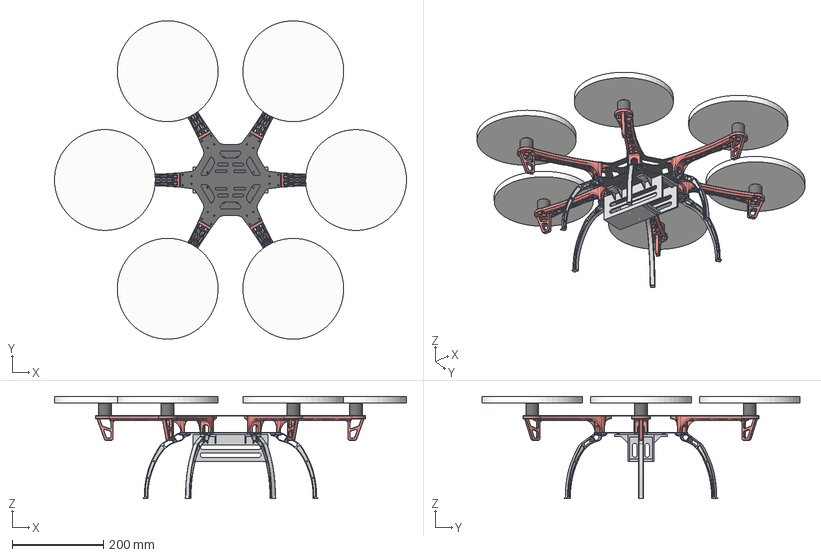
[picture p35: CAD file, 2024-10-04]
System_development/Jocassee/V0.6.0/UAV model/UAV fully assembled.step
771.1 x 697.5 x 223.6 mm
F450 Arm x 6
F550 Top Plate
e310_motor x 6
e310_prop x 6
F550 Bottom Plate
Battery Housing v1
Landing leg v1 x 6

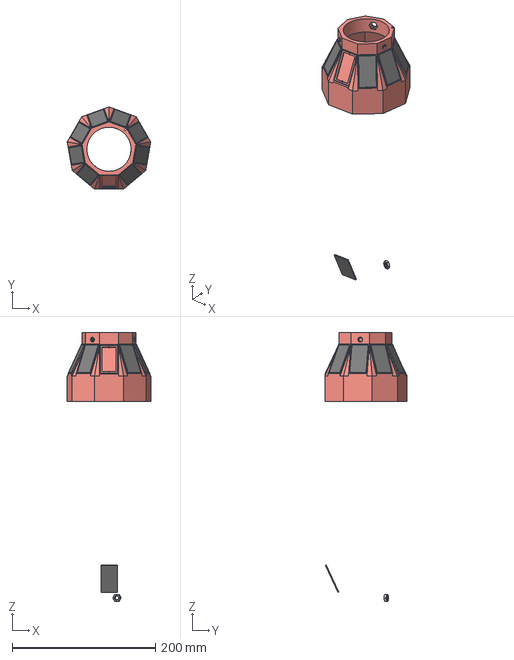
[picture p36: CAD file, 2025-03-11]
System_development/Jocassee/V0.6.0/Component CAD files/Buoy v3 (75 degree inclined).step
116.8 x 115.1 x 375.6 mm
Solar panel (1) x 9
GRAINGER-38DG47 x 3

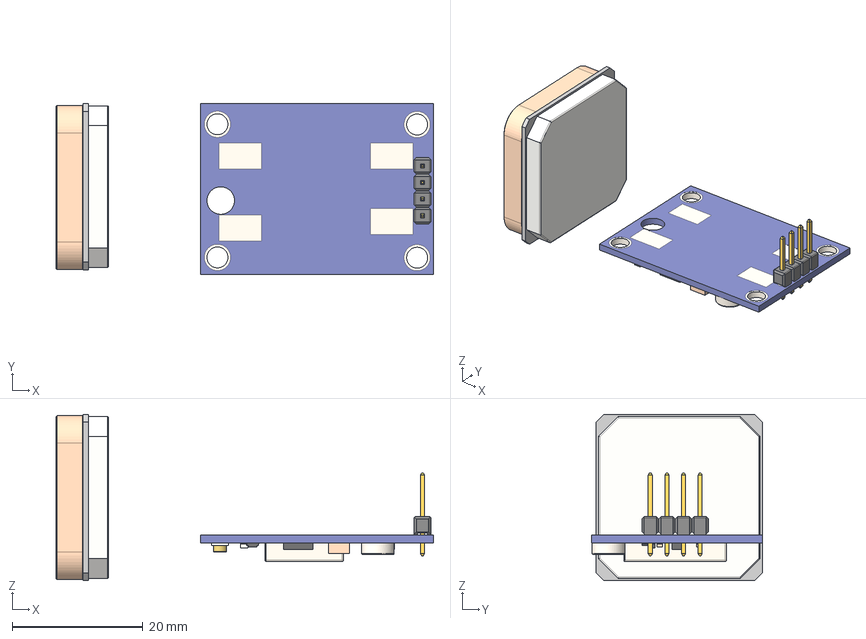
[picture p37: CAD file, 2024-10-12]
System_development/Jocassee/V0.6.0/EDA/Initial prototype/3D models/GY-NEO6MV2-withAnt v7.step
57.9 x 26.1 x 25.4 mm
Pin Header 1x4 TH Pitch 2.54mm

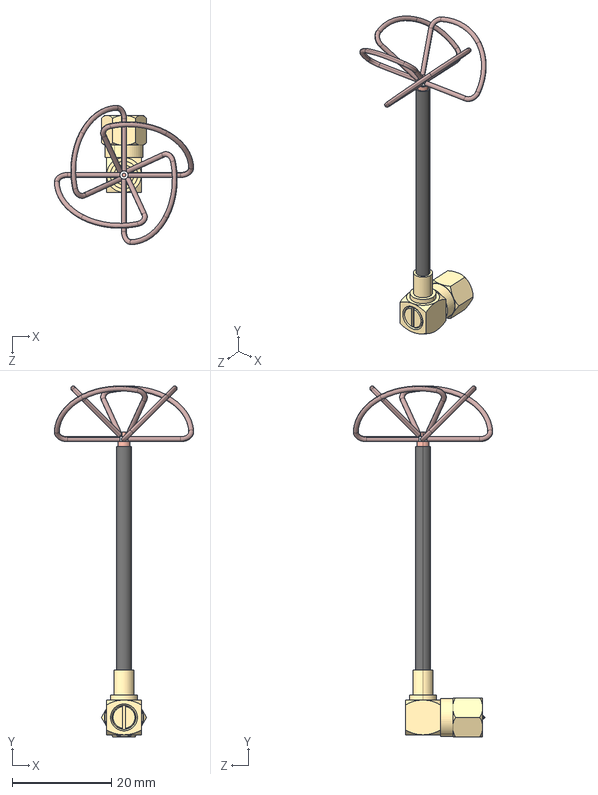
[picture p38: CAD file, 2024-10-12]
System_development/Jocassee/V0.6.0/EDA/Initial prototype/3D models/NRF24/SP_antenna.STEP
28.1 x 70.7 x 28.1 mm
Lobe_SPW x 4
ANT_Base_�� 㬮�砭��
ANT_Nut_�� 㬮�砭��
ANT_SetScrew_�� 㬮�砭��

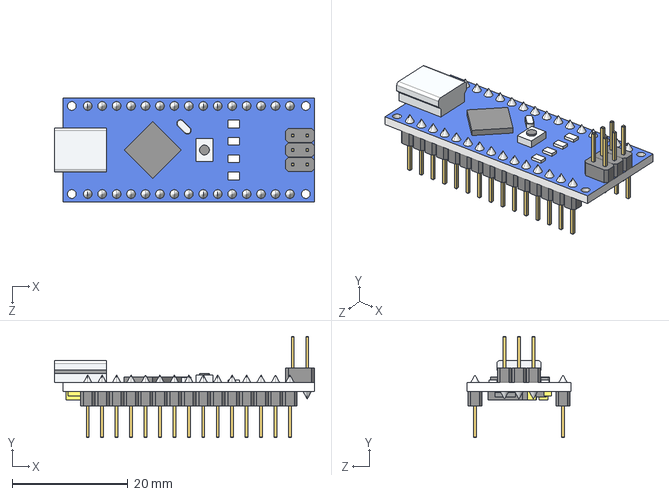
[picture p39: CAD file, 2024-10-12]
System_development/Jocassee/V0.6.0/EDA/V0.6.3/3D models/Arduino_Nano.STEP
45.0 x 17.5 x 18.0 mm

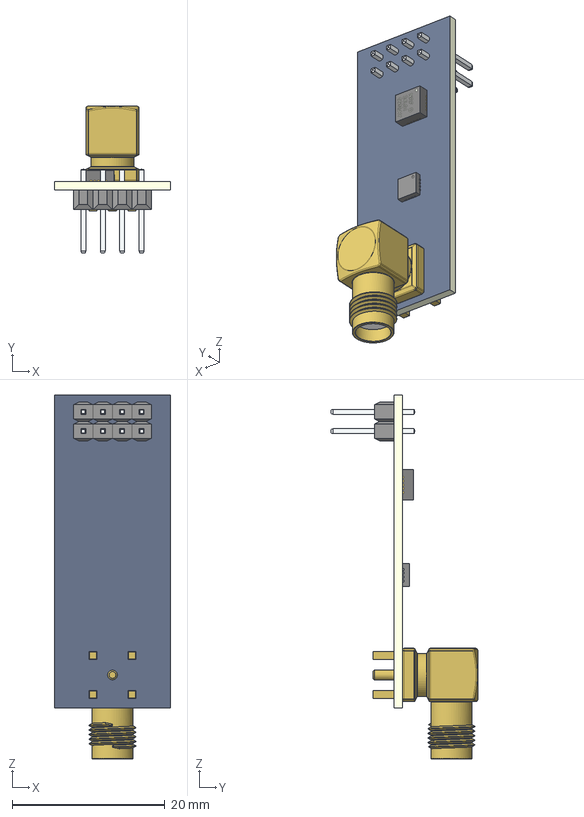
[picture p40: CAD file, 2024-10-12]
System_development/Jocassee/V0.6.0/EDA/V0.6.3/3D models/NRF24/NRF24l01_with_antenna.STEP
15.2 x 19.3 x 47.6 mm
NRF24L01_PCB
male header x 8
NRF24L01_SMA-angled
NRF24L01-CHIP-NRF___ _________
User Library-QFN-16_3x3_1
User Library-QFN-16_3x3_2
User Library-QFN-16_3x3_3
User Library-QFN-16_3x3_4
User Library-QFN-16_3x3_5
User Library-QFN-16_3x3_6
User Library-QFN-16_3x3_7
User Library-QFN-16_3x3_8
User Library-QFN-16_3x3_9
User Library-QFN-16_3x3_10
User Library-QFN-16_3x3_11
User Library-QFN-16_3x3_12
User Library-QFN-16_3x3_13
User Library-QFN-16_3x3_14
User Library-QFN-16_3x3_15
User Library-QFN-16_3x3_16
User Library-QFN-16_3x3_17
User Library-QFN-16_3x3_18

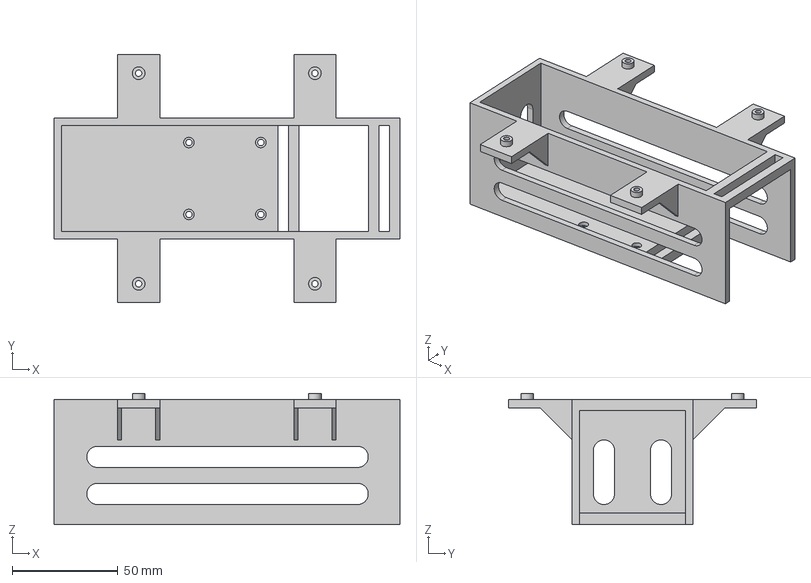
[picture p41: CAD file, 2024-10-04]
System_development/Jocassee/V0.6.0/UAV model/Battery Housing.step
163.5 x 117.0 x 62.0 mm

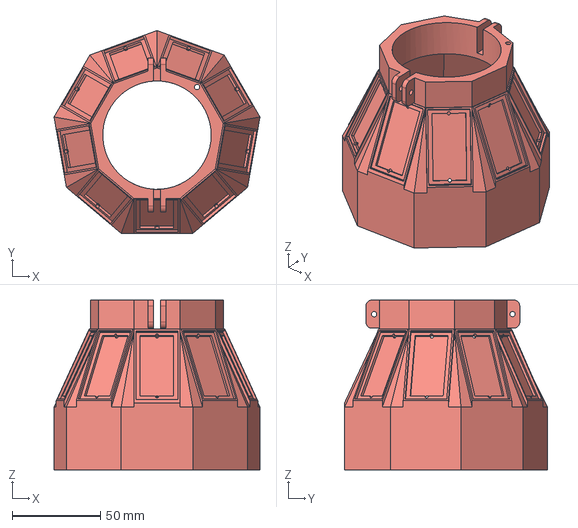
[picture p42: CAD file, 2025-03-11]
System_development/Jocassee/V0.6.0/Component CAD files/Buoy v3.9 (75 degree).step
116.8 x 115.1 x 96.4 mm

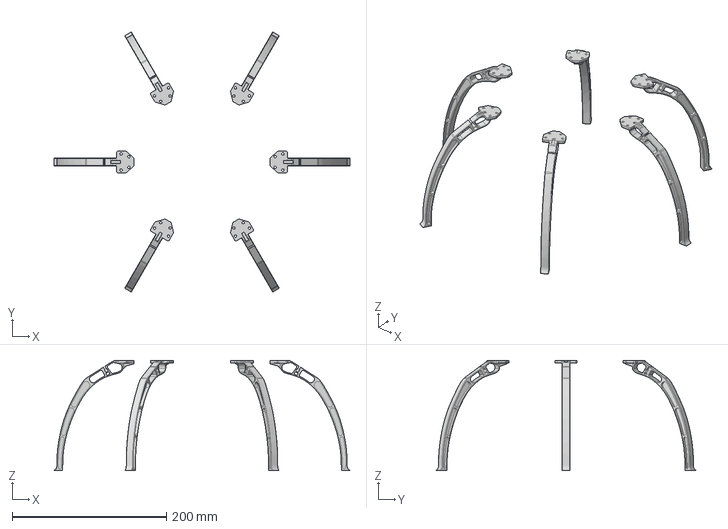
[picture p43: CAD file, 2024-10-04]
System_development/Jocassee/V0.6.0/UAV model/Landing legs.step
384.1 x 337.3 x 143.3 mm
Landing leg v1 x 6

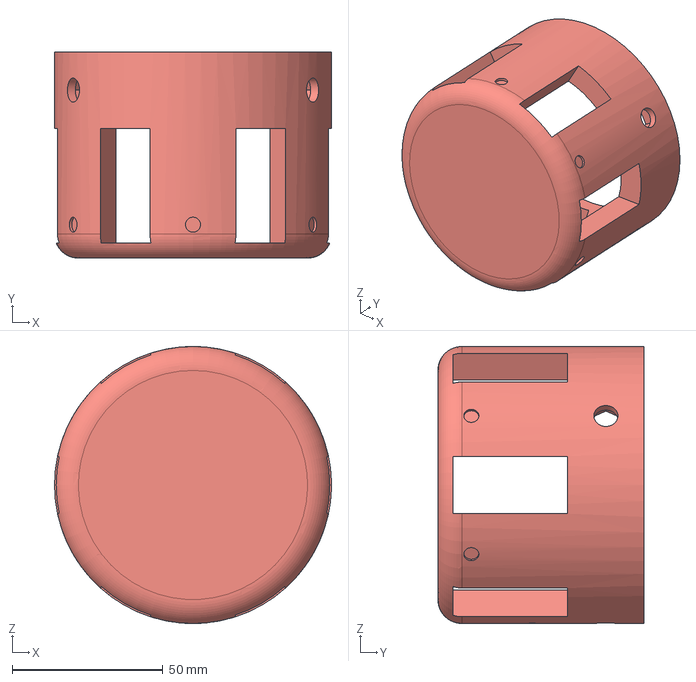
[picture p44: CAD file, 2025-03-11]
System_development/Jocassee/V0.6.0/Component CAD files/Printable Grate v1.step
92.0 x 68.5 x 92.0 mm

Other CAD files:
System_development/Jocassee/V0.1/Case_design/Connector bottom cap v34.f3d
System_development/Jocassee/V0.1/Case_design/Solar wing v10.f3d
System_development/Jocassee/V0.1/Case_design/connector cap v26.f3d
System_development/Jocassee/V0.1/Case_design/sensor package case v30.f3d
System_development/Jocassee/V0.1/Case_design/solar connection v13.f3d
System_development/Jocassee/V0.1/Case_design/turbidity case v6.f3d
System_development/Jocassee/V0.2/Case_design/Connector bottom cap v34.f3d
System_development/Jocassee/V0.2/Case_design/Solar wing v10.f3d
System_development/Jocassee/V0.2/Case_design/connector cap v26.f3d
System_development/Jocassee/V0.2/Case_design/sensor package case v30.f3d
System_development/Jocassee/V0.2/Case_design/solar connection v13.f3d
System_development/Jocassee/V0.2/Case_design/turbidity case v6.f3d
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

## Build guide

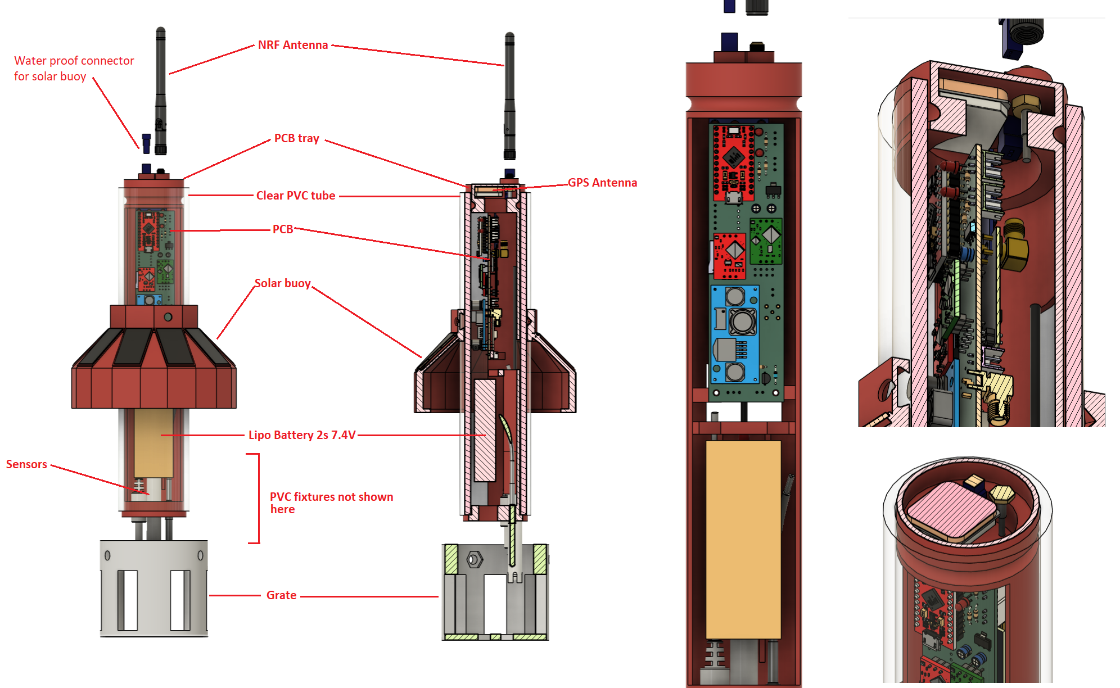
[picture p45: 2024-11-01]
System_development/Jocassee/V0.6.0/Component CAD files/Full Assembly image.png

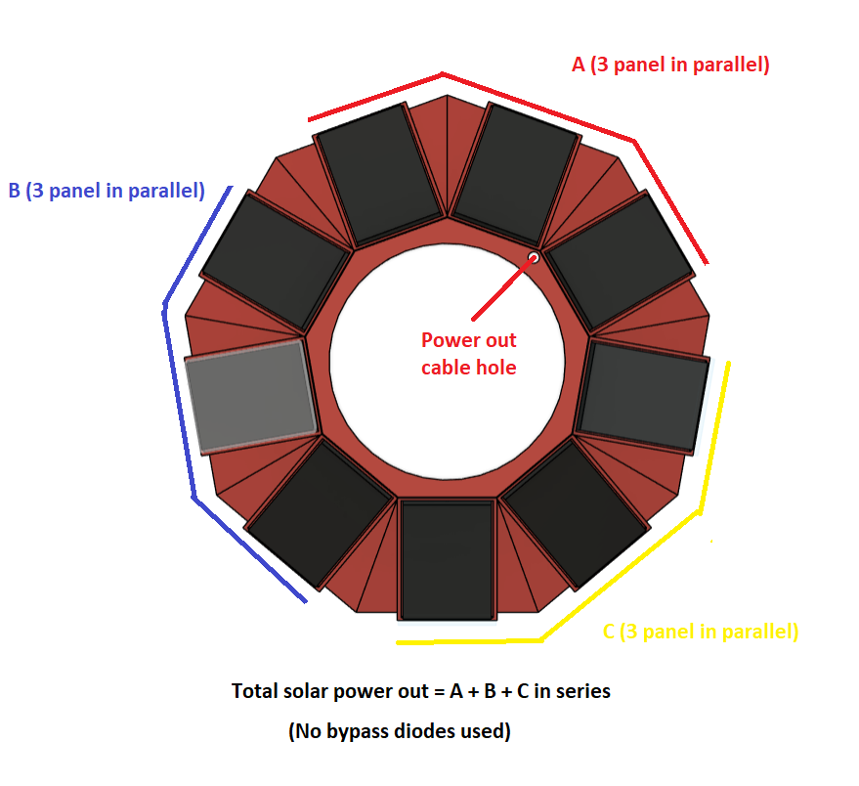
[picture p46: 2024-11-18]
System_development/Jocassee/V0.6.0/EDA/Solar Panel wiring combination.png

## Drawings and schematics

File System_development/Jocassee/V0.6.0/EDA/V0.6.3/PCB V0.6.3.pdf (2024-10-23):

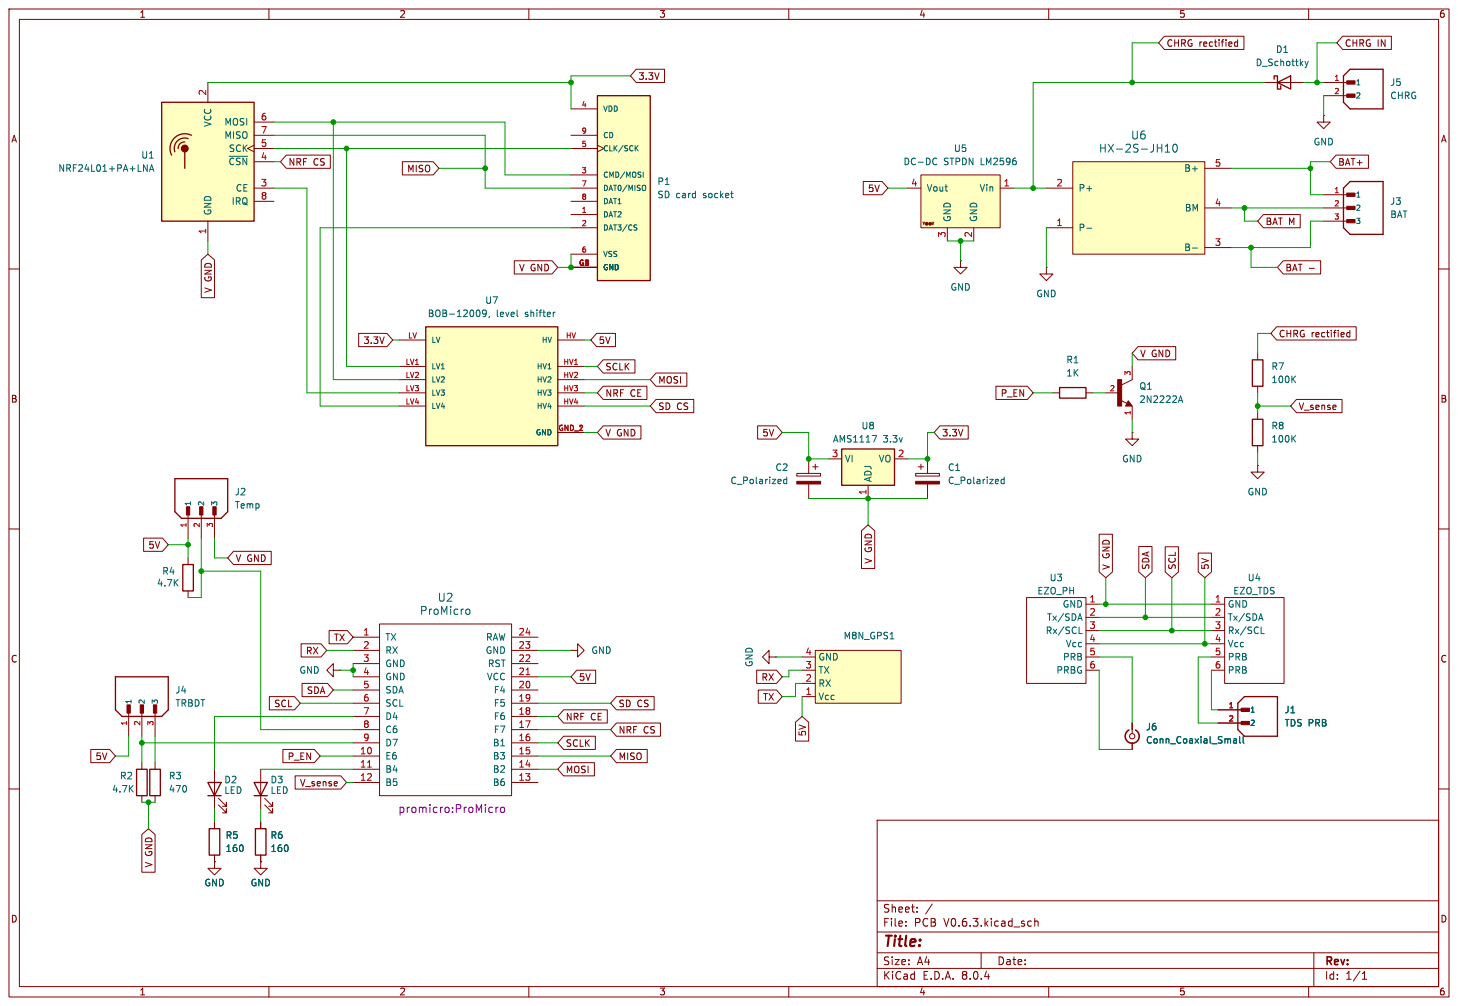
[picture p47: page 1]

2 CE 3 ~{CSN} 4 SCK 5 MOSI 6 MISO 7

3 Vout 4 U5 DC-DC STPDN LM2596 GND

SD CS NRF CE

SD CS NRF CS

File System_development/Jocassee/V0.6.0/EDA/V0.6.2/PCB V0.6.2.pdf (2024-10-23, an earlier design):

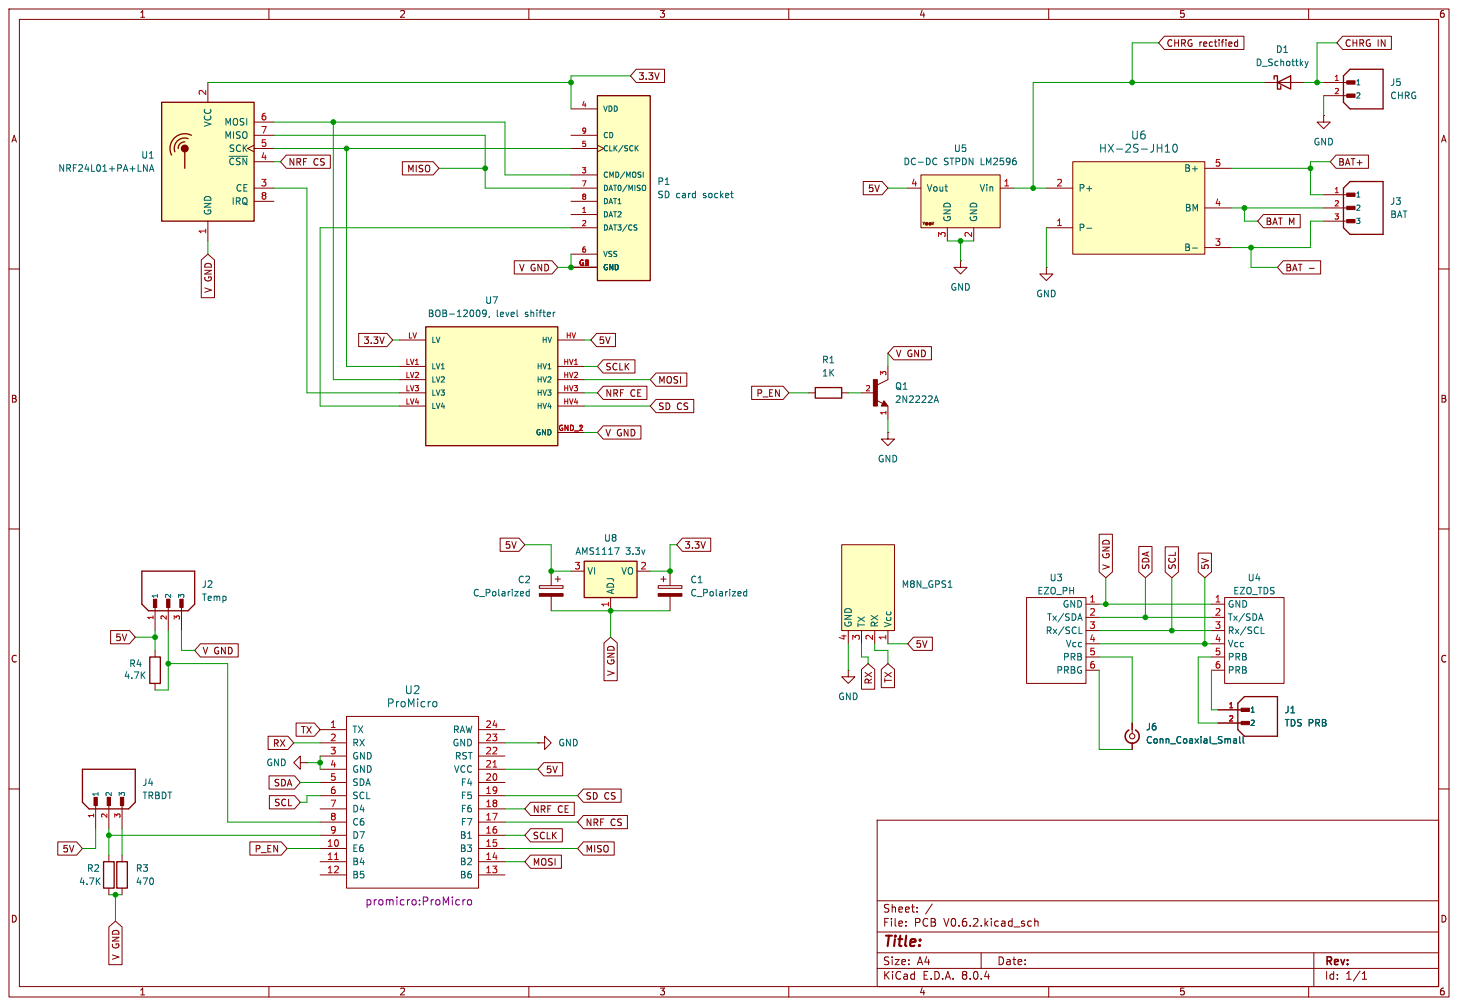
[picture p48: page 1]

V GND SDA CHRG IN
BAT+ 5V

2 CE 3 ~{CSN} 4 SCK 5 MOSI 6 MISO 7

3 Vout 4 U5 DC-DC STPDN LM2596

SD CS NRF CE

NRF CS NRF CE

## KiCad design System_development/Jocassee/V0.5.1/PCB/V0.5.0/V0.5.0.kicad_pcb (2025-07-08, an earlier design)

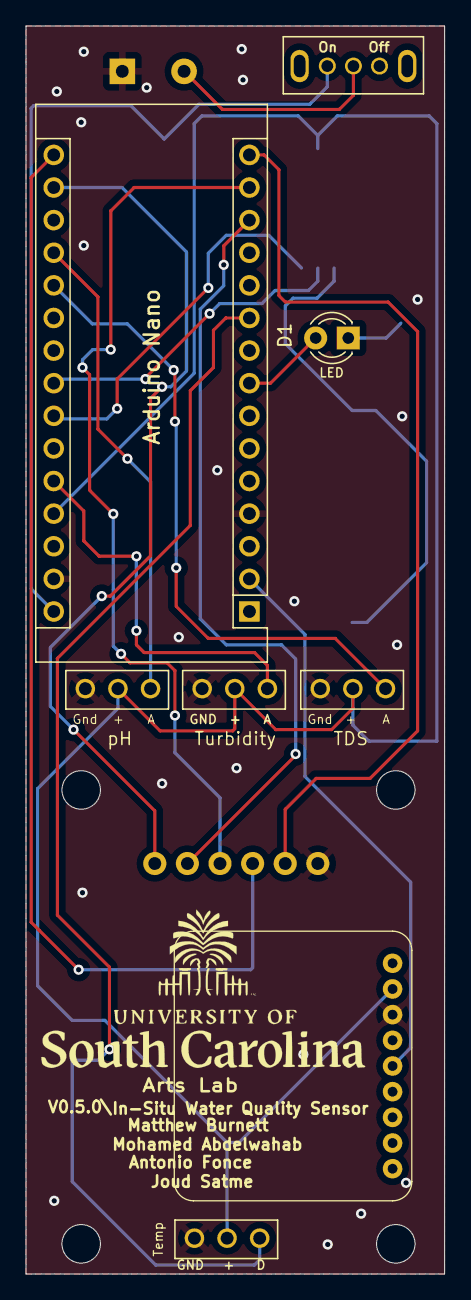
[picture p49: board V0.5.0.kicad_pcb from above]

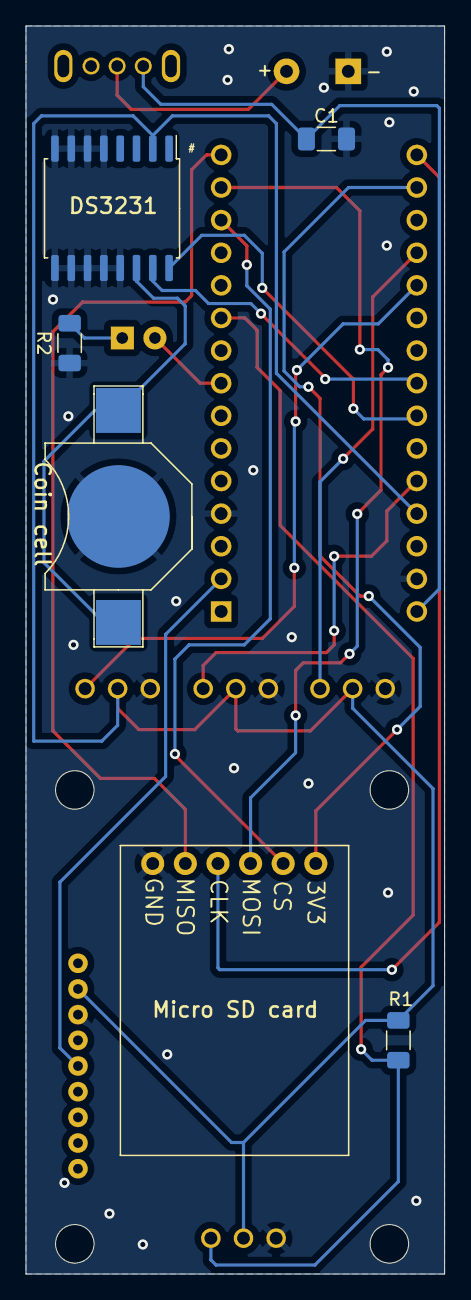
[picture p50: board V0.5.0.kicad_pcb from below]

Board: 2 copper layers, 32.6 x 97.2 mm, 15 parts (7 on the bottom side), 19 nets.

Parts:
A1: Arduino_Nano_v3.x; Arduino_Nano
BT1: Battery_Cell; battery_holder_10mm
C1: C; C_1206_3216Metric_Pad1.33x1.80mm_HandSolder
D1: LED; LED_D3.0mm
R1, R2: R; R_1206_3216Metric_Pad1.30x1.75mm_HandSolder
U1: water_Battery; Battery_Input
U2: SD
U3: switch; grounded_switch
U4: pH; phraails
U5: Sensor; TDS
U6: DS3231M; SOIC-16W_7.5x10.3mm_P1.27mm
U7: Sensor; Turbidity
U8: Temp; Temp.
U9: GPS Module

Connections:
GND: A1.4 (GND), A1.29 (GND), BT1.2 (-), C1.2, R2.2, U1.2 (Gnd), U2.6 (GND), U4.1 (GND), U5.1 (GND), U6.5 (GND), U6.6 (GND), U6.7 (GND), U6.8 (GND), U6.9 (GND), U6.10 (GND), U6.11 (GND), U6.12 (GND), U6.13 (GND), U7.1 (GND), U8.1 (Gnd), U9.7 (GND)
unnamed: A1.17 (3V3), U2.1 (3V)
unnamed: A1.27 (+5V), R1.2, U4.2 (+), U5.2 (+), U6.2 (VCC), U7.2 (+), U8.2 (5V), U9.8 (VIN)
unnamed: A1.19 (A0), U4.3 (A)
unnamed: A1.20 (A1), U5.3 (A)
unnamed: A1.23 (A4), U6.15 (SDA)
unnamed: A1.24 (A5), U6.16 (SCL)
unnamed: A1.26 (A7), U7.3 (A)
unnamed: A1.2 (D0/RX), U9.5 (TX)
unnamed: A1.8 (D5), D1.2 (A)
unnamed: A1.10 (D7), R1.1, U8.3 (D)
unnamed: A1.13 (D10), U2.2 (CS)
unnamed: A1.14 (D11), U2.3 (Mosi)
unnamed: A1.15 (D12), U2.5 (Miso)
unnamed: A1.16 (D13), U2.4 (CLK)
unnamed: A1.30 (VIN), C1.1, U3.3 (PO)
unnamed: BT1.1 (+), U6.14 (VBAT)
unnamed: D1.1 (K), R2.1
unnamed: U1.1 (Power), U3.2 (PI)

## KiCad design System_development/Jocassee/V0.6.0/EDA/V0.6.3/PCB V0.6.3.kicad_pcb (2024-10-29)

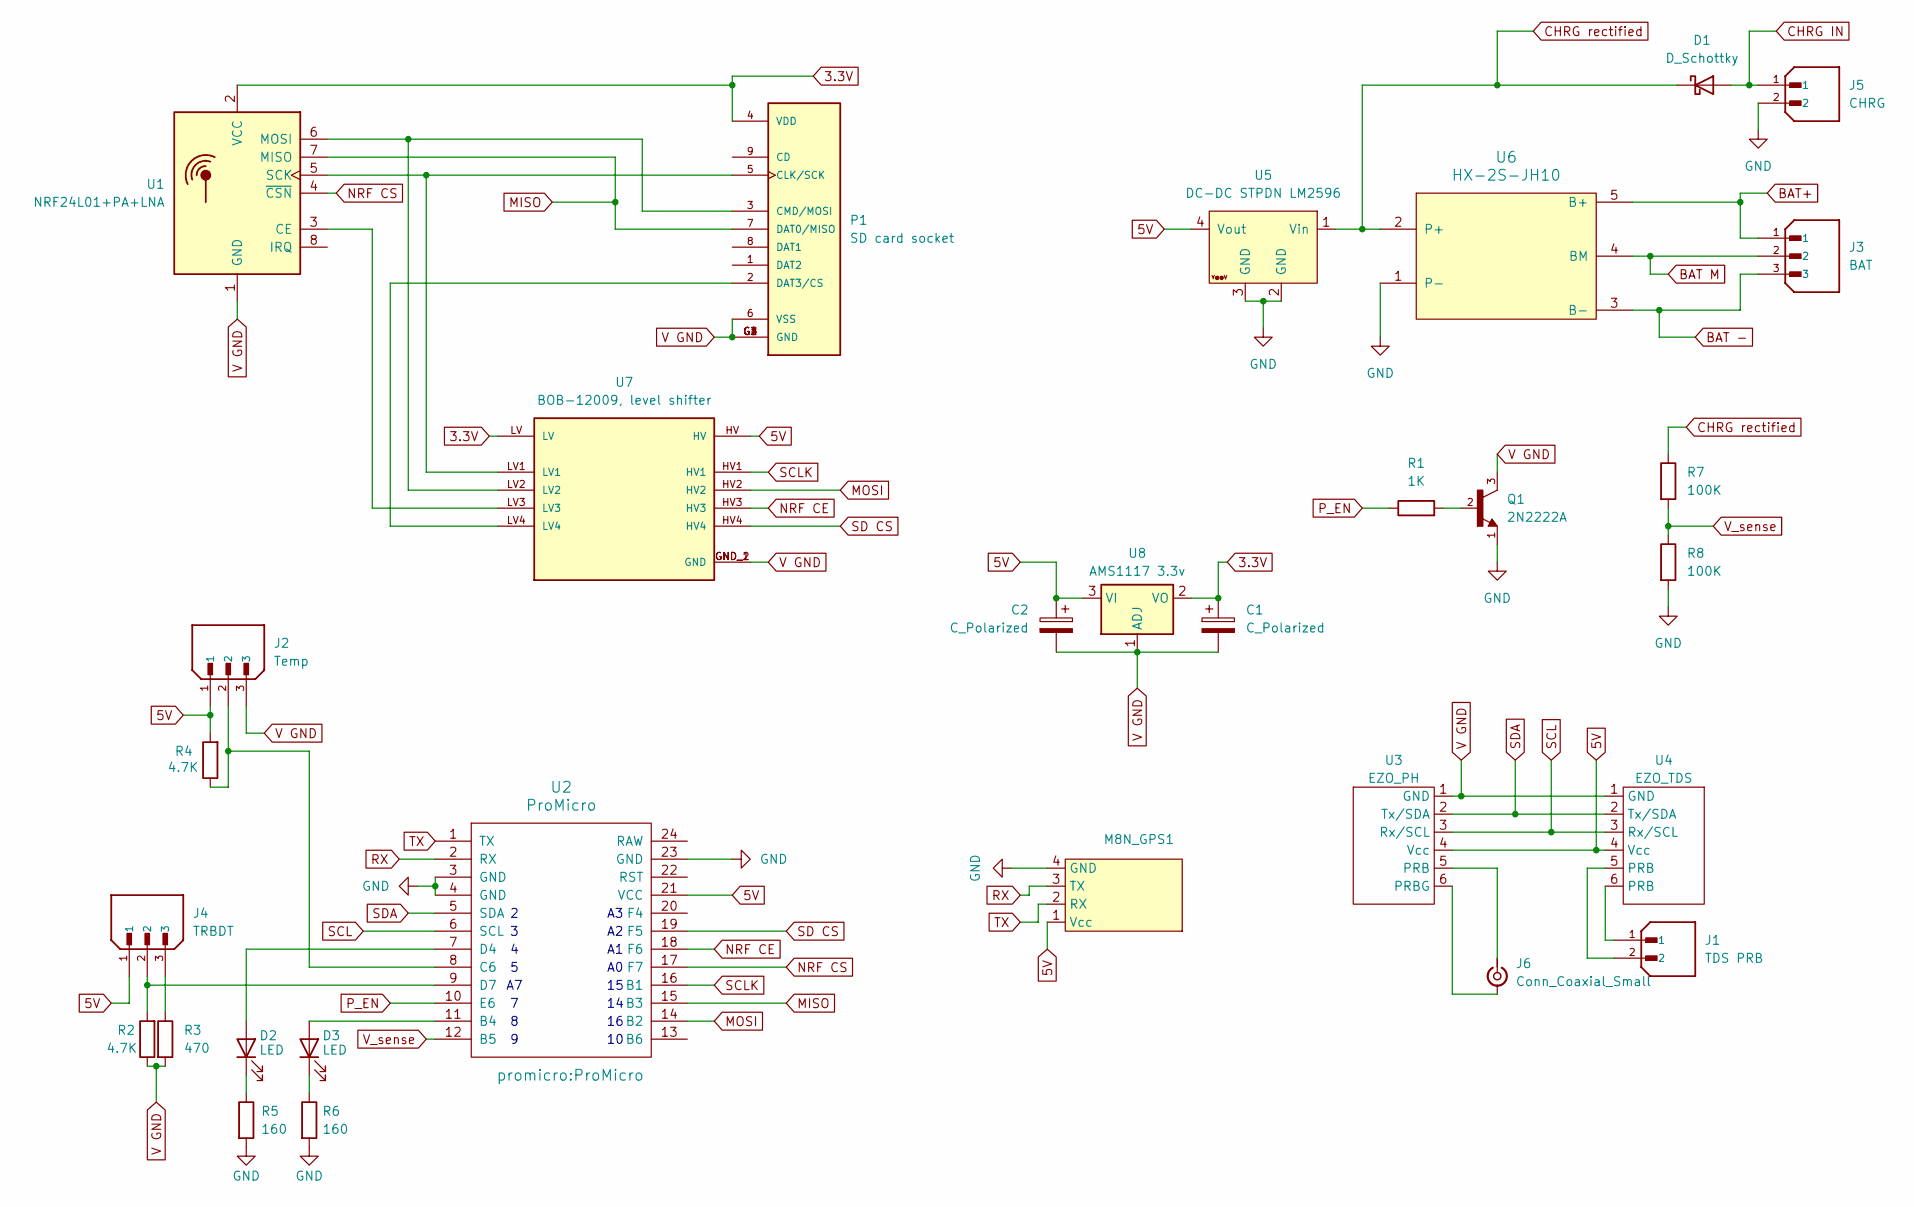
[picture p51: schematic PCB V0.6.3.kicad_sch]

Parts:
C1, C2: C_Polarized; CP_Radial_D4.0mm_P2.00mm
D1: D_Schottky; D_DO-34_SOD68_P7.62mm_Horizontal
D2, D3: LED; LED_D3.0mm
J1: TDS PRB; JST_B2B-XH-A_LF__SN_; PARTREV N/A
J2: Temp; XH2.54; PARTREV 7/4/21
J3: BAT; XH2.54; PARTREV 7/4/21
J4: TRBDT; XH2.54; PARTREV 7/4/21
J5: CHRG; JST_B2B-XH-A_LF__SN_; PARTREV N/A
J6: Conn_Coaxial_Small; SMA_Amphenol_901-143_Horizontal
M8N_GPS1: Ublox_Neo_M8N_GPS
P1: SD card socket; SUNTECH_ST-TF-003A
Q1: 2N2222A; TO92254P470H750-3; PARTREV N/A
R1: 1K; R_Axial_DIN0204_L3.6mm_D1.6mm_P5.08mm_Horizontal
R2: 4.7K; R_Axial_DIN0204_L3.6mm_D1.6mm_P7.62mm_Horizontal
R3: 470; R_Axial_DIN0204_L3.6mm_D1.6mm_P7.62mm_Horizontal
R4: 4.7K; R_Axial_DIN0204_L3.6mm_D1.6mm_P5.08mm_Horizontal
R5, R6: 160; R_Axial_DIN0204_L3.6mm_D1.6mm_P7.62mm_Horizontal
R7, R8: 100K; R_Axial_DIN0204_L3.6mm_D1.6mm_P5.08mm_Horizontal
U1: NRF24L01+PA+LNA; NRF24L01+PA/LNA-FOOTPRINT
U2: ProMicro
U3: EZO_PH
U4: EZO_TDS
U5: DC-DC STPDN LM2596; YAAJ_DCDC_StepDown_LM2596
U6: HX-2S-JH10
U7: BOB-12009, level shifter; Logic_level_shifter; PARTREV 01
U8: AMS1117 3.3v; SOT-223-3_TabPin2

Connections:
3.3V: C1.1, P1.4 (VDD), U1.2 (VCC), U7.LV, U8.2 (VO)
5V: C2.1, J2.1, J4.1, M8N_GPS1.1 (Vcc), R4.2, U2.21 (VCC), U3.4 (Vcc), U4.4 (Vcc), U5.4 (Vout), U7.HV, U8.3 (VI)
BAT -: J3.3, U6.3 (B-)
BAT M: J3.2, U6.4 (BM)
BAT+: J3.1, U6.5 (B+)
CHRG IN: D1.2 (A), J5.1
CHRG rectified: D1.1 (K), R7.1, U5.1 (Vin), U6.2 (P+)
GND: J5.2, M8N_GPS1.4 (GND), Q1.1, R5.2, R6.2, R8.2, U2.3 (GND), U2.4 (GND), U2.23 (GND), U5.2 (GND), U5.3 (GND), U6.1 (P-)
MISO: P1.7 (DAT0/MISO), U1.7 (MISO), U2.15 (B3)
MOSI: U2.14 (B2), U7.HV2
NRF CE: U2.18 (F6), U7.HV3
NRF CS: U1.4 (~CSN), U2.17 (F7)
unnamed: D2.2 (A), U2.7 (D4)
unnamed: D2.1 (K), R5.1
unnamed: D3.2 (A), U2.11 (B4)
unnamed: D3.1 (K), R6.1
unnamed: J1.1, U4.6 (PRB)
unnamed: J1.2, U4.5 (PRB)
unnamed: J4.3, R3.1
unnamed: J6.2 (Ext), U3.6 (PRBG)
unnamed: J6.1 (In), U3.5 (PRB)
unnamed: P1.5 (CLK/SCK), U1.5 (SCK), U7.LV1
unnamed: P1.3 (CMD/MOSI), U1.6 (MOSI), U7.LV2
unnamed: P1.2 (DAT3/CS), U7.LV4
unnamed: Q1.2, R1.2
unnamed: U1.3 (CE), U7.LV3
unnamed: J2.2, R4.1, U2.8 (C6)
unnamed: J4.2, R2.2, U2.9 (D7)
P_EN: R1.1, U2.10 (E6)
RX: M8N_GPS1.3 (TX), U2.2 (RX)
SCL: U2.6 (SCL), U3.3 (Rx/SCL), U4.3 (Rx/SCL)
SCLK: U2.16 (B1), U7.HV1
SD CS: U2.19 (F5), U7.HV4
SDA: U2.5 (SDA), U3.2 (Tx/SDA), U4.2 (Tx/SDA)
TX: M8N_GPS1.2 (RX), U2.1 (TX)
V GND: C1.2, C2.2, J2.3, P1.6 (VSS), P1.G1 (GND), P1.G2 (GND), P1.G3 (GND), P1.G4 (GND), Q1.3, R2.1, R3.2, U1.1 (GND), U3.1 (GND), U4.1 (GND), U7.GND_1 (GND), U7.GND_2 (GND), U8.1 (ADJ)
V_sense: R7.2, R8.1, U2.12 (B5)

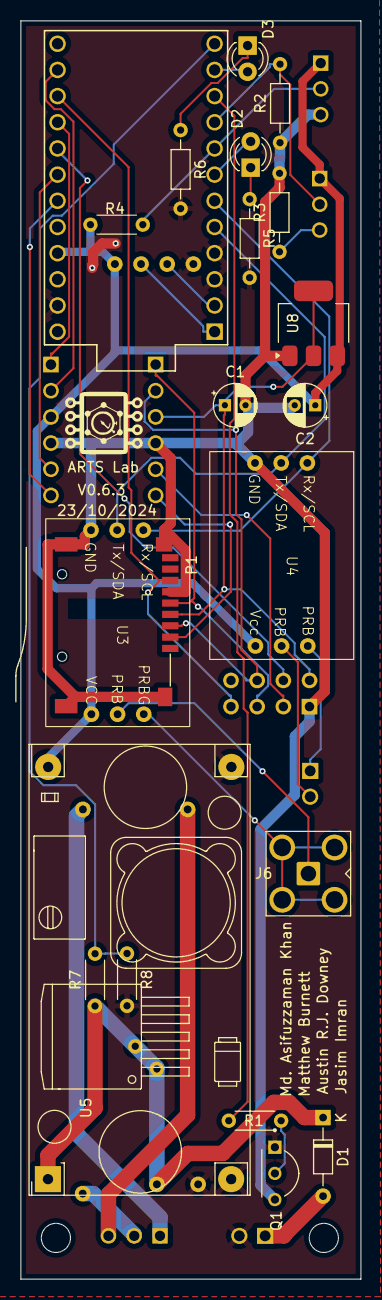
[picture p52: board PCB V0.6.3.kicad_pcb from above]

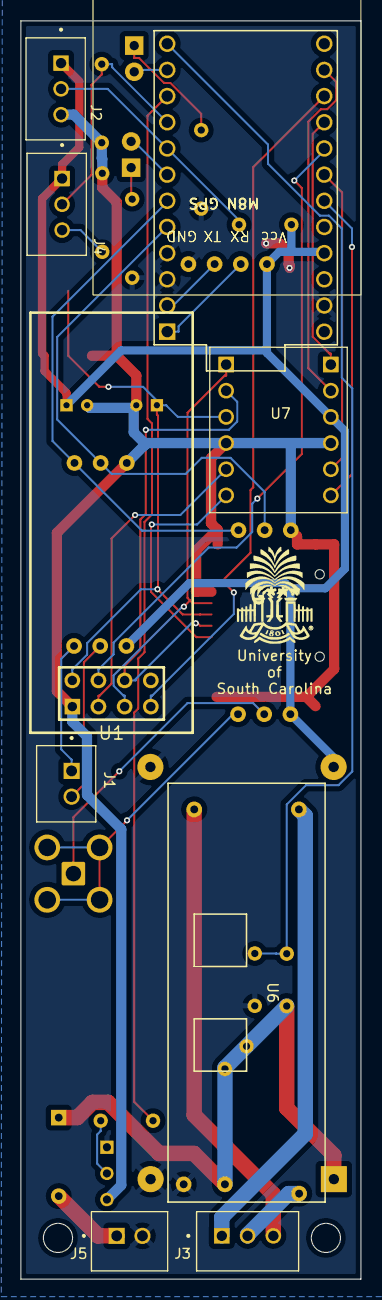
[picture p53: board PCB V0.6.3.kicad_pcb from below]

Board: 2 copper layers, 33.0 x 122.1 mm, 31 parts (9 on the bottom side), 37 nets.

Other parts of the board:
ARTS Lab: LOGO

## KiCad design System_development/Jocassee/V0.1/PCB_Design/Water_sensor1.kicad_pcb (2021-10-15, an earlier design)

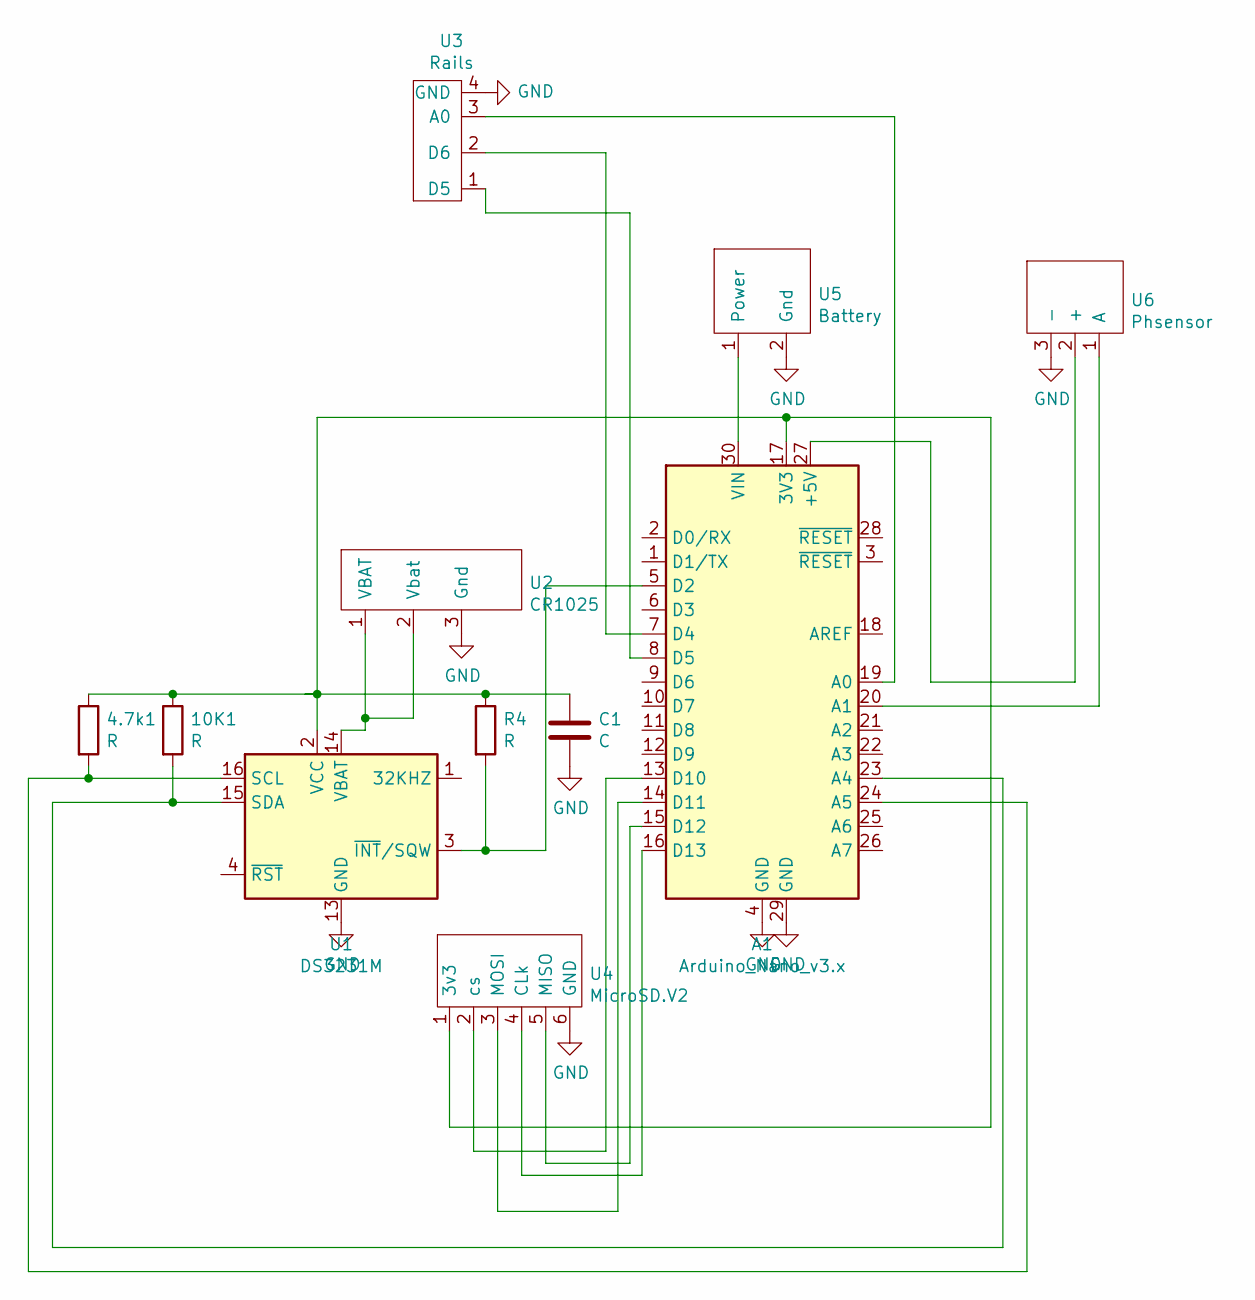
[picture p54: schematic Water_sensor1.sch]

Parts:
4.7k1, 10K1: R; R_1206_3216Metric
A1: Arduino_Nano_v3.x; Arduino_Nano
C1: C; C_1206_3216Metric
R4: R; R_1206_3216Metric
U1: DS3231M; SOIC-16W_7.5x10.3mm_P1.27mm
U2: CR1025
U3: Rails
U4: MicroSD.V2
U5: Battery; battery
U6: Phsensor; PH_meter

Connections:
GND: A1.4 (GND), A1.29 (GND), C1.2, U1.5 (GND), U1.6 (GND), U1.7 (GND), U1.8 (GND), U1.9 (GND), U1.10 (GND), U1.11 (GND), U1.12 (GND), U1.13 (GND), U2.3 (Gnd), U3.4 (GND), U4.6 (GND), U5.2 (Gnd), U6.3 (-)
unnamed: 4.7k1.2, A1.24 (A5), U1.16 (SCL)
unnamed: 4.7k1.1, 10K1.1, A1.17 (3V3), C1.1, R4.1, U1.2 (VCC), U4.1 (3v3)
unnamed: 10K1.2, A1.23 (A4), U1.15 (SDA)
unnamed: A1.5 (D2), R4.2, U1.3 (~INT~/SQW)
unnamed: A1.7 (D4), U3.2 (D6)
unnamed: A1.8 (D5), U3.1 (D5)
unnamed: A1.13 (D10), U4.2 (cs~)
unnamed: A1.14 (D11), U4.3 (MOSI)
unnamed: A1.15 (D12), U4.5 (MISO)
unnamed: A1.16 (D13), U4.4 (CLk)
unnamed: A1.19 (A0), U3.3 (A0)
unnamed: A1.20 (A1), U6.1 (A)
unnamed: A1.27 (+5V), U6.2 (+)
unnamed: A1.30 (VIN), U5.1 (Power)
unnamed: U1.14 (VBAT), U2.1 (VBAT), U2.2 (Vbat)

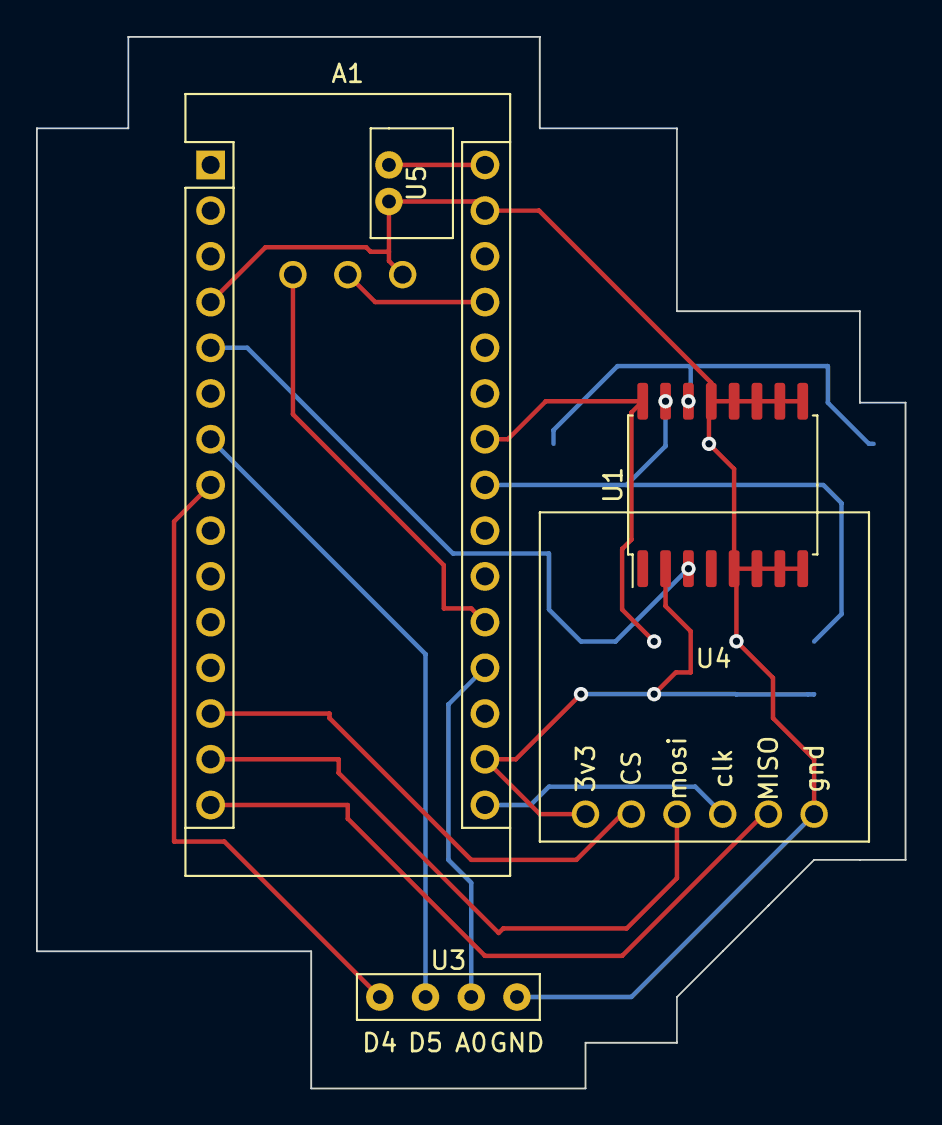
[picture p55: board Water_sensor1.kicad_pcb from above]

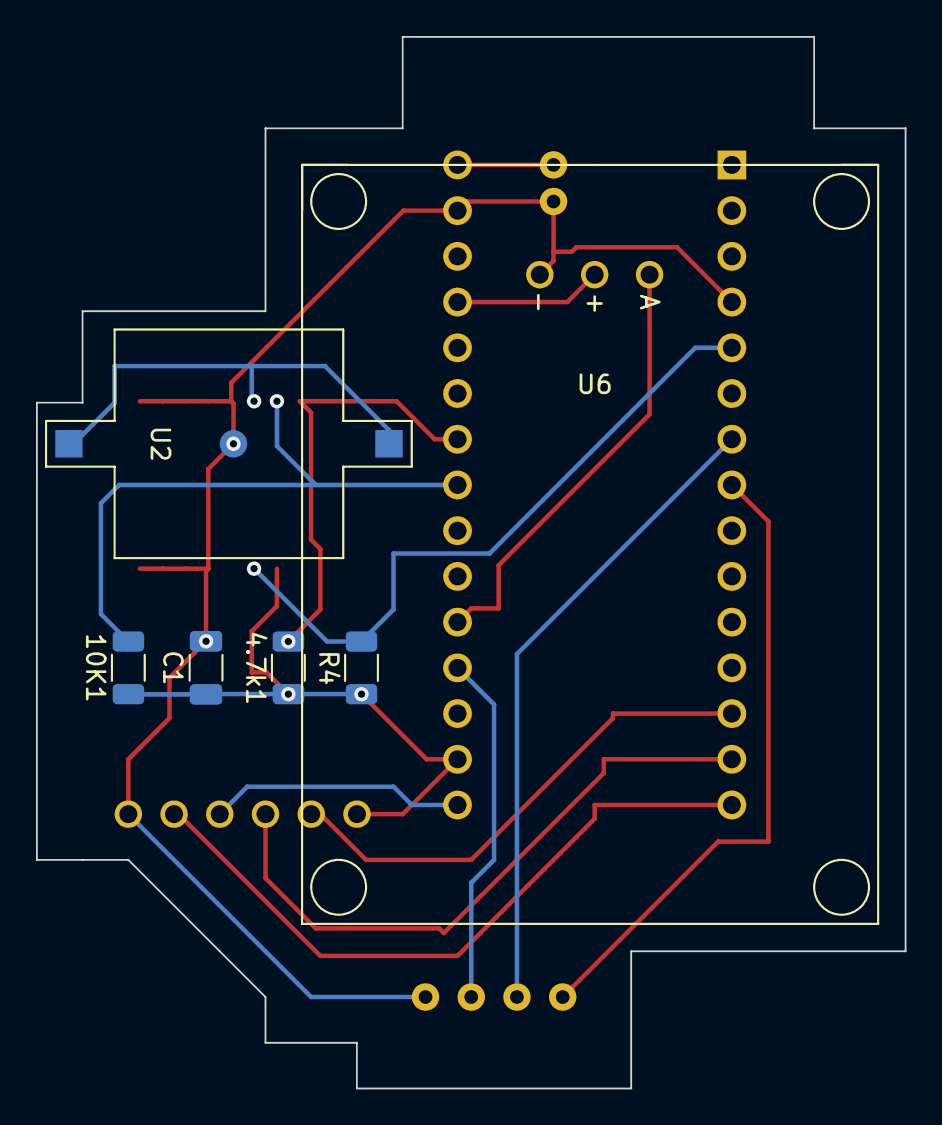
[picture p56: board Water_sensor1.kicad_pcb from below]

Board: 2 copper layers, 48.3 x 58.4 mm, 11 parts (6 on the bottom side), 16 nets.

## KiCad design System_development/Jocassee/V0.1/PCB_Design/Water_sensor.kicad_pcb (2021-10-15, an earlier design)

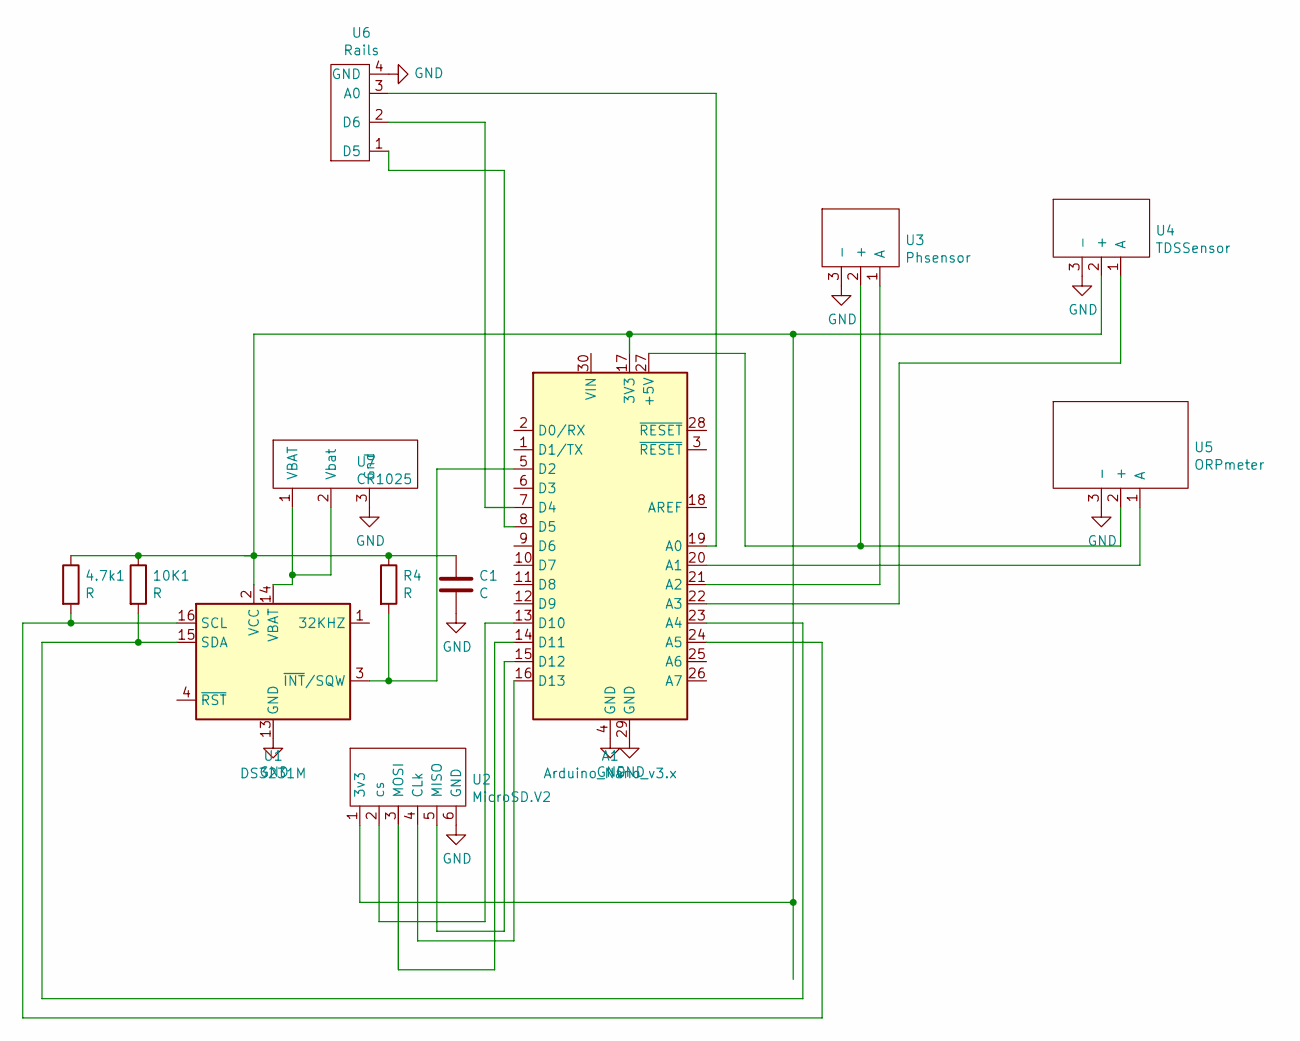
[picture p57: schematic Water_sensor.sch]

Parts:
4.7k1, 10K1: R; R_1206_3216Metric
A1: Arduino_Nano_v3.x; Arduino_Nano
C1: C; C_1206_3216Metric
R4: R; R_1206_3216Metric
U1: DS3231M; SOIC-16W_7.5x10.3mm_P1.27mm
U2: MicroSD.V2
U3: Phsensor; PH_meter
U4: TDSSensor; TDS_meter
U5: ORPmeter; ORP_meter
U6: Rails
U7: CR1025

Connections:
GND: A1.4 (GND), A1.29 (GND), C1.2, U1.5 (GND), U1.6 (GND), U1.7 (GND), U1.8 (GND), U1.9 (GND), U1.10 (GND), U1.11 (GND), U1.12 (GND), U1.13 (GND), U2.6 (GND), U3.3 (-), U4.3 (-), U5.3 (-), U6.4 (GND), U7.3 (Gnd)
unnamed: 4.7k1.2, A1.24 (A5), U1.16 (SCL)
unnamed: 4.7k1.1, 10K1.1, A1.17 (3V3), C1.1, R4.1, U1.2 (VCC), U2.1 (3v3), U4.2 (+)
unnamed: 10K1.2, A1.23 (A4), U1.15 (SDA)
unnamed: A1.5 (D2), R4.2, U1.3 (~INT~/SQW)
unnamed: A1.7 (D4), U6.2 (D6)
unnamed: A1.8 (D5), U6.1 (D5)
unnamed: A1.13 (D10), U2.2 (cs~)
unnamed: A1.14 (D11), U2.3 (MOSI)
unnamed: A1.15 (D12), U2.5 (MISO)
unnamed: A1.16 (D13), U2.4 (CLk)
unnamed: A1.19 (A0), U6.3 (A0)
unnamed: A1.20 (A1), U5.1 (A)
unnamed: A1.21 (A2), U3.1 (A)
unnamed: A1.22 (A3), U4.1 (A)
unnamed: A1.27 (+5V), U3.2 (+), U5.2 (+)
unnamed: U1.14 (VBAT), U7.1 (VBAT), U7.2 (Vbat)

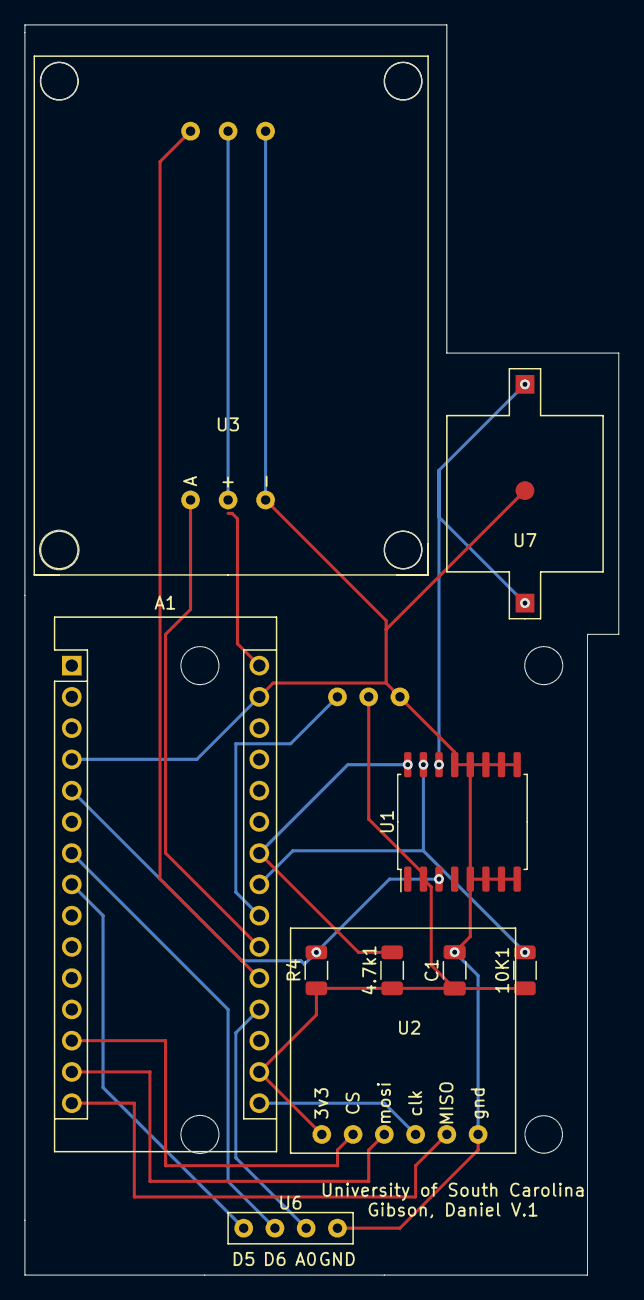
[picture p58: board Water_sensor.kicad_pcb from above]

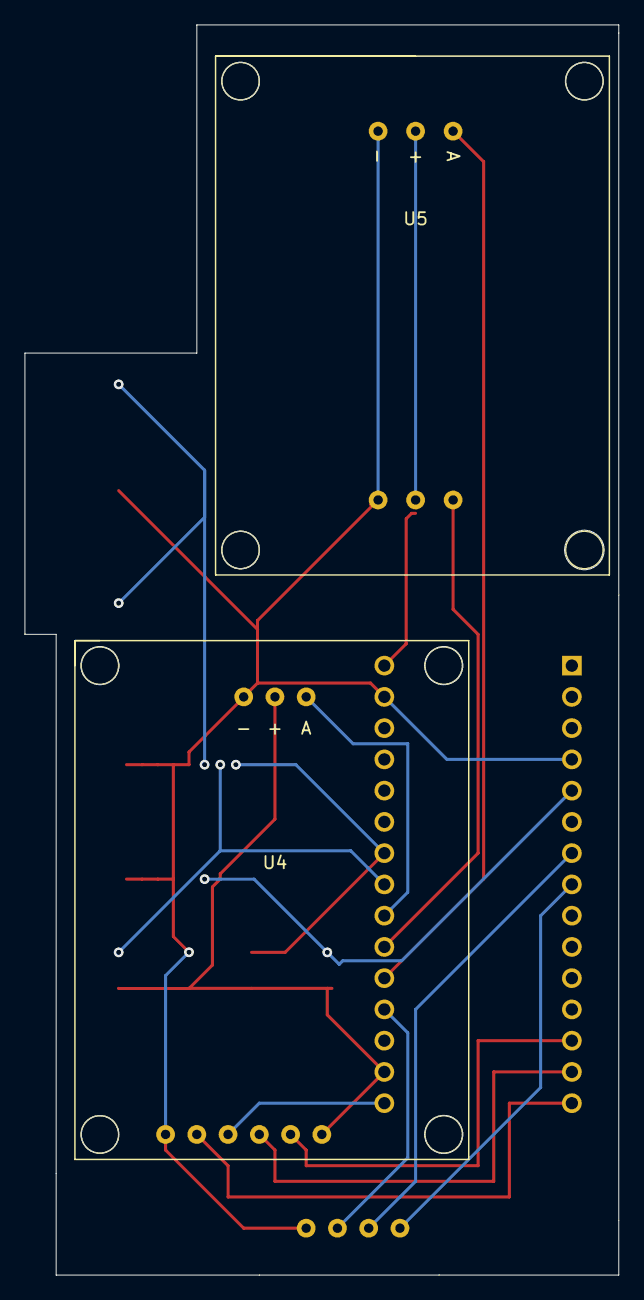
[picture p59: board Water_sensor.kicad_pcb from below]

Board: 2 copper layers, 48.3 x 101.6 mm, 12 parts (2 on the bottom side), 17 nets.

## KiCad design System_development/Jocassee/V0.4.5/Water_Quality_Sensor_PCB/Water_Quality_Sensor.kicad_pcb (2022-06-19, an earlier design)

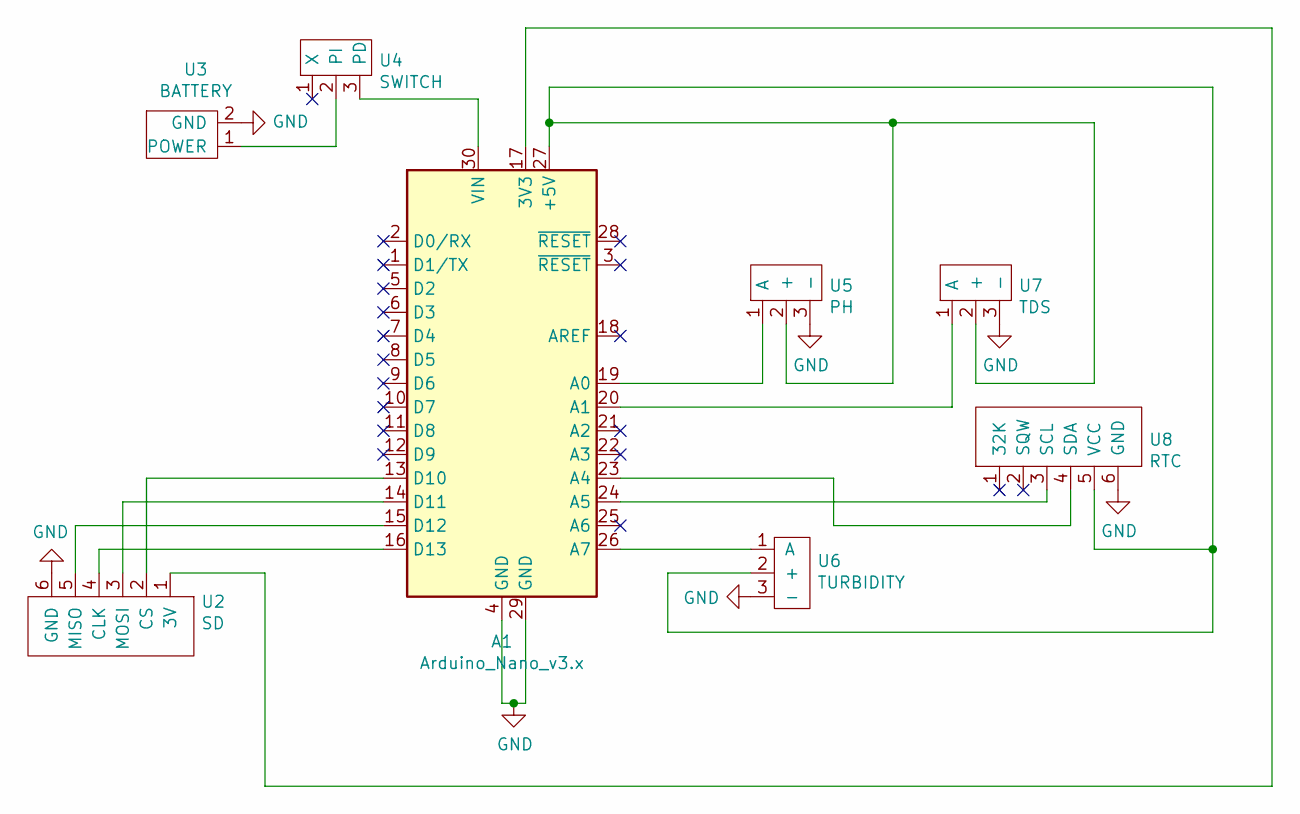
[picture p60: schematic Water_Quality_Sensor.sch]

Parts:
A1: Arduino_Nano_v3.x; Arduino_Nano
U2: SD
U3: BATTERY; battery_input
U4: SWITCH; slide_switch
U5: PH; phraails
U6: TURBIDITY; turbidity_rails
U7: TDS; sensor_rails
U8: RTC

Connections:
GND: A1.4 (GND), A1.29 (GND), U2.6 (GND), U3.2 (GND), U5.3 (-), U6.3 (-), U7.3 (-), U8.6 (GND)
unnamed: A1.13 (D10), U2.2 (CS)
unnamed: A1.14 (D11), U2.3 (MOSI)
unnamed: A1.15 (D12), U2.5 (MISO)
unnamed: A1.16 (D13), U2.4 (CLK)
unnamed: A1.17 (3V3), U2.1 (3V)
unnamed: A1.19 (A0), U5.1 (A)
unnamed: A1.20 (A1), U7.1 (A)
unnamed: A1.23 (A4), U8.4 (SDA)
unnamed: A1.24 (A5), U8.3 (SCL)
unnamed: A1.26 (A7), U6.1 (A)
unnamed: A1.27 (+5V), U5.2 (+), U6.2 (+), U7.2 (+), U8.5 (VCC)
unnamed: A1.30 (VIN), U4.3 (PD)
unnamed: U3.1 (POWER), U4.2 (PI)


Board: 2 copper layers, 44.0 x 58.5 mm, 9 parts (1 on the bottom side), 14 nets.

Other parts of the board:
R1: R; uofsc_logo_0_75in

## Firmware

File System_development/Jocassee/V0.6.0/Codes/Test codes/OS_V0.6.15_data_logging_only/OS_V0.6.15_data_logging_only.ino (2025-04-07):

/*
 * This is a demo operating system of In-situ Water Quality Sensor V0.6.0
 * Author: Md. Asifuzzaman Khan
 * Date: January 29, 2025

 © Adaptive Real-Time Systems Laboratory
 University of South Carolina
 300 Main St., Columbia, SC.
 */

#include "Lib_and_def.h";

void setup() {

  pinMode(LED_BUILTIN_TX, OUTPUT);    
  digitalWrite(LED_BUILTIN_TX, HIGH); // turn off TX light
  pinMode(LED_BUILTIN_RX, INPUT);     // turn off RX light
  
  //delay(3000);
  pinMode(P_En, OUTPUT);
  pinMode(Red_LED, OUTPUT);
  pinMode(Yellow_LED, OUTPUT);
  digitalWrite(P_En,LOW);
  digitalWrite(Red_LED,LOW);
  digitalWrite(Yellow_LED,LOW);
  Serial.begin(115200);
}

#include "Functions.h";
void loop() {
  check_bat_volt();
  //get_gps_data();
  power_peripheral(1);
  read_pH_and_EC();
  read_TRBDT();
  read_temp();
  write2SD();
  power_peripheral(0);

  delay(26000);
  
}

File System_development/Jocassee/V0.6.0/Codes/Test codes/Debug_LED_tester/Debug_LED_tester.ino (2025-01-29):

/*
  Blink

  Turns an LED on for one second, then off for one second, repeatedly.

  Most Arduinos have an on-board LED you can control. On the UNO, MEGA and ZERO
  it is attached to digital pin 13, on MKR1000 on pin 6. LED_BUILTIN is set to
  the correct LED pin independent of which board is used.
  If you want to know what pin the on-board LED is connected to on your Arduino
  model, check the Technical Specs of your board at:
  https://www.arduino.cc/en/Main/Products

  modified 8 May 2014
  by Scott Fitzgerald
  modified 2 Sep 2016
  by Arturo Guadalupi
  modified 8 Sep 2016
  by Colby Newman

  This example code is in the public domain.

  https://www.arduino.cc/en/Tutorial/BuiltInExamples/Blink
*/
#define LED1 8
#define LED2 4
// the setup function runs once when you press reset or power the board
void setup() {
  // initialize digital pin LED_BUILTIN as an output.
  pinMode(LED1, OUTPUT);
  pinMode(LED2, OUTPUT);
}

// the loop function runs over and over again forever
void loop() {
  digitalWrite(LED1, LOW);
  digitalWrite(LED2, HIGH);// turn the LED on (HIGH is the voltage level)
  delay(500);                       // wait for a second
  digitalWrite(LED1, HIGH);
  digitalWrite(LED2, LOW);// turn the LED off by making the voltage LOW
  delay(500);                       // wait for a second
}

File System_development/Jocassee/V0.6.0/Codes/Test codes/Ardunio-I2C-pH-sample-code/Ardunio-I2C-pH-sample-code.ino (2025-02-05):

//This code will work on an Arduino Uno and Mega
//This code was written to be easy to understand.
//Modify this code as you see fit.
//This code will output data to the Arduino serial monitor.
//Type commands into the Arduino serial monitor to control the Ph circuit.
//This code was written in the Arduino 2.3.2 IDE
//This code was last tested 9/24


#include <Wire.h>                //enable I2C.
#define address 99               //default I2C ID number for EZO pH Circuit.

char computerdata[20];           //we make a 20 byte character array to hold incoming data from a pc/mac/other.
byte received_from_computer = 0; //we need to know how many characters have been received.
byte code = 0;                   //used to hold the I2C response code.
char ph_data[32];                //we make a 32 byte character array to hold incoming data from the pH circuit.
byte in_char = 0;                //used as a 1 byte buffer to store inbound bytes from the pH Circuit.
byte i = 0;                      //counter used for ph_data array.
int time_ = 815;                 //used to change the delay needed depending on the command sent to the EZO Class pH Circuit.
float ph_float;                  //float var used to hold the float value of the pH.


void setup()                     //hardware initialization.
{
  Serial.begin(9600);           //enable serial port.
  Wire.begin();                 //enable I2C port.
}


void loop() {                                                                     //the main loop.
  if (Serial.available()) {                                                     //if a command was sent to the EZO device.

    received_from_computer = Serial.readBytesUntil(13, computerdata, 20);           //we read the data sent from the serial monitor(pc/mac/other) until we see a <CR>. We also count how many characters have been received.
    computerdata[received_from_computer] = 0;                                       //stop the buffer from transmitting leftovers or garbage.

    for (i = 0; i <= received_from_computer; i++) {                               //set all char to lower case, this is just so this exact sample code can recognize the "sleep" command.
      computerdata[i] = tolower(computerdata[i]);                                 //"Sleep" ≠ "sleep"
    }
    i=0;                                                                          //reset i, we will need it later 
    if (computerdata[0] == 'c' || computerdata[0] == 'r')time_ = 815;             //if a command has been sent to calibrate or take a reading we wait 815ms so that the circuit has time to take the reading.
    else time_ = 250;                                                             //if any other command has been sent we wait only 250ms.
    

    Wire.beginTransmission(address);                                              //call the circuit by its ID number.
    Wire.write(computerdata);                                                     //transmit the command that was sent through the serial port.
    Wire.endTransmission();                                                       //end the I2C data transmission.


    if (strcmp(computerdata, "sleep") != 0) {  	                                  //if the command that has been sent is NOT the sleep command, wait the correct amount of time and request data.
                                                                                  //if it is the sleep command, we do nothing. Issuing a sleep command and then requesting data will wake the circuit.

      delay(time_);								                                                //wait the correct amount of time for the circuit to complete its instruction.

      Wire.requestFrom(address, 32, 1); 		                                      //call the circuit and request 32 bytes (this may be more than we need)
      code = Wire.read();               		                                      //the first byte is the response code, we read this separately.

      switch (code) {							          //switch case based on what the response code is.
        case 1:                         		//decimal 1.
          Serial.println("Success");    		//means the command was successful.
          break;                        		//exits the switch case.

        case 2:                         		//decimal 2.
          Serial.println("Failed");     		//means the command has failed.
          break;                        		//exits the switch case.

        case 254:                       		//decimal 254.
          Serial.println("Pending");    		//means the command has not yet been finished calculating.
          break;                        		//exits the switch case.

        case 255:                       		//decimal 255.
          Serial.println("No Data");    		//means there is no further data to send.
          break;                        		//exits the switch case.
      }





      while (Wire.available()) {         		//are there bytes to receive.
        in_char = Wire.read();           		//receive a byte.
        ph_data[i] = in_char;					      //load this byte into our array.
        i += 1;                          		//incur the counter for the array element.
        if (in_char == 0) {              		//if we see that we have been sent a null command.
          i = 0;                         		//reset the counter i to 0.
          break;                         		//exit the while loop.
        }
      }

      Serial.println(ph_data);          		//print the data.
    }
  }
  //Uncomment this section if you want to take the pH value and convert it into floating point number.
  //ph_float=atof(ph_data);
}

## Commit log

2021-10-15 created v.0.0.3
    [Connector bottom cap v34.f3d, Solar wing v10.f3d, Water_sensor-B_Cu.gbr, Water_sensor-B_Mask.gbr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]
2021-11-04 Gibson, Daniel
    [Ph_sensor.kicad_pcb, Ph_sensor.sch, mainboard-B_Cu.gbr, mainboard-B_Mask.gbr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]
2022-03-21 clean up the files
    [Acrylic tube.stp, Battery tray.stp, Connector bottom cap v34 (1).step, Connector bottom cap v34.f3d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]
2022-03-21 folder updates
    [Acrylic tube.stp, Battery tray.stp, Connector bottom cap v34 (1).step, Connector bottom cap v34.f3d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]
2022-03-21 changes made to layout
    [Acrylic tube.stp, Battery tray.stp, Connector bottom cap v34 (1).step, Connector bottom cap v34.f3d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]
2022-05-05 cleaned up files.
    [Acrylic tube.CATPart, Acrylic tube.stp, Battery tray.CATPart, Battery tray.stp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]
2022-06-18 Water Quality Sensor V0.5
    [PCBINSITU.kicad_pcb, PCBINSITU.sch]
2022-06-18 Water Quality Sensor
    [PCBINSITU.kicad_pcb, PCBINSITU.sch]
2022-06-21 Water Quality sensor V0.4.5 update
    [Water_Quality_Sensor.kicad_pcb, Water_Quality_Sensor.sch]
2022-06-21 Water Quality Sensor V0.4.5
    [Water_Quality_Sensor.kicad_pcb, Water_Quality_Sensor.sch]
2022-06-21 Water Quality Sensor PCB
    [Water_Quality_Sensor.kicad_pcb, Water_Quality_Sensor.sch]
2022-06-21 added v0.4.6
    [Acrylic tube.CATPart, Acrylic tube.stp, Battery tray.CATPart, Battery tray.stp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]
2022-06-27 Water Quality Sensor fusion 360 files
    [Acrylic tube v1.f3d, Battery tray v1.f3d, PCB Tray v1.f3d, PCB v1.f3d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]
2023-05-26 Updated PCB design and Arduino cpde
    [Final_Design-B_Cu.gbr, Final_Design-B_Mask.gbr, Final_Design-B_Paste.gbr, Final_Design-B_SilkS.gbr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]
2023-06-21 PCB & Battery Tray CAD Design
    [PCB_&_Battery_Tray v9.f3d]
2023-08-13 Updated layout and main readme
    [Acrylic tube v1.f3d, Acrylic tube.CATPart, Acrylic tube.stp, Battery tray v1.f3d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]
2023-08-15 System Design Files for V0.4.6
    [Final_Design-B_Cu.gbr, Final_Design-B_Mask.gbr, Final_Design-B_Paste.gbr, Final_Design-B_SilkS.gbr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]
2024-05-03 Cleaned up repo layout, added high-level versions.
    [Acrylic tube v1.f3d, Acrylic tube.CATPart, Acrylic tube.stp, Battery tray v1.f3d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]
2024-05-12 removed un-needed folders
    [V0.1-B_Cu.gbr, V0.1-B_Mask.gbr, V0.1-B_Paste.gbr, V0.1-B_SilkS.gbr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]
2024-06-13 Added GPS
    Added a GPS module to the PCB board
    [PCB_&_Battery_Tray v9.f3d, V0.1-B_Cu.gbr, V0.1-B_Mask.gbr, V0.1-B_Paste.gbr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]
2024-06-17 Made Bouy and Hinge and Leaf cad files
    [Connector and Hidnges.ipt, Hinge and Leaf Assembly.iam, Leaf.ipt, V0.1.csv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]
2024-06-17 Updated Bill of Materials and added Buoy 2
    [Water Sensor Bouy 1.ipt, Water Sensor Bouy 2.0008.ipt, Water Sensor Bouy 2.ipt, Water Sensor Bouy.0007.ipt]
2024-06-17 Updated the Water Sensor Buoy models
    [Water Sensor Bouy 1.0008.ipt, Water Sensor Bouy 1.ipt, Water Sensor Bouy 2.0008.ipt, Water Sensor Bouy 2.0011.ipt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]
2024-06-17 Updated Claps for Buoys
    [Water Sensor Bouy 1.0008.ipt, Water Sensor Bouy 1.0009.ipt, Water Sensor Bouy 1.ipt, Water Sensor Bouy 2.0011.ipt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]
2024-06-17 Uploaded STL files
    [Water Sensor Bouy 1.0009.ipt, Water Sensor Bouy 1.0011.ipt, Water Sensor Bouy 1.ipt, Water Sensor Bouy 1.stl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]
2024-06-24 Added another Buoy design and reorganized files
    Added another buoy design and an assembly to better scale the buoys. Also reorganized the files to include only what is needed.
    [Assembled Water Sensor Chassi.0001.iam, Assembled Water Sensor Chassi.iam, Connector and Hidnges.ipt, Hinge and Leaf Assembly.iam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]
2024-06-24 Removed files for V0.4.7 from V0.4.6
    Removed files meant for V0.4.7 from V0.4.6 after accidental inclusion
    [V0.2 Rough Draft Schematic.kicad_sch, V0.2 Rough Draft-B_Cu.gbr, V0.2 Rough Draft-B_Mask.gbr, V0.2 Rough Draft-B_Paste.gbr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]
2024-06-24 Added Buoy 3 and 4
    Added designs for water sensor buoys 3 and 4
    [Water Sensor Bouy 3.0007.ipt, Water Sensor Bouy 3.0009.ipt, Water Sensor Bouy 3.ipt, Water Sensor Bouy 3.stl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]
2024-06-24 Fixed Buoy 4
    Fixed the inner radius on the Buoy 4
    [Water Sensor Bouy 4.0001.ipt, Water Sensor Bouy 4.0002.ipt, Water Sensor Bouy 4.ipt, Water Sensor Bouy 4.stl]
2024-06-26 Updated Buoy and cap designs
    Updated the buoy designs to have thinner walls and updated the cap design to have O-ring slots. Also added all buoys to the Chassis Assembly.
    [Assembled Water Sensor Chassi.0001.iam, Assembled Water Sensor Chassi.0002.iam, Assembled Water Sensor Chassi.iam, Water Sensor Bouy 1.0013.ipt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]
2024-07-01 Updated Cad Files
    Updated the CAD files for the Water Sensor Cap and PCB tray, added Buoys 5, 6, and 7. Updated BOM
    [Assembled Water Sensor Chassi.0002.iam, Assembled Water Sensor Chassi.0003.iam, Assembled Water Sensor Chassi.iam, Buoy 5 HalfSphere.0003.ipt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]
2024-07-02 Updated PCB Tray and BOM
    [PCB tray CAD.0003.ipt, PCB tray CAD.0007.ipt, PCB tray CAD.ipt, PCB tray CAD.stl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]
2024-07-10 Made CAD assembly of water sensor chassi with components
    Made an assembly with the water sensor chassi including all the components except the buoy. Added a new folder for this addition and reorganized other folders.
    [Arc Water Sensor.ipt, Assembled Water Sensor Chassi.0003.iam, Assembled Water Sensor Chassi.0005.iam, Assembled Water Sensor Chassi.iam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]
2024-07-12 Changed PCB tray
    Made PCB tray longer and added a Battery tray insert. Also separated PCB tray into a bottom and top parts for ease of use. Added a Cad model for spacers for PCB. Updated Arc sensor and water sensor c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
    [Arc Water Sensor.0002.ipt, Arc Water Sensor.ipt, Assembled Water Sensor Chassi.0006.iam, Assembled Water Sensor Chassi.iam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]
2024-07-15 Updated PCB tray and Water Sensor Cap
    [Assembled Water Sensor Chassi.0006.iam, Assembled Water Sensor Chassi.0007.iam, Assembled Water Sensor Chassi.iam, PCB Battery Tray.0004.ipt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]
2024-07-17 Updated PCB board tray, Spacer for PCB, and Water Sensor Cap
    [PCB Battery Tray.0007.ipt, PCB Battery Tray.0008.ipt, PCB Battery Tray.ipt, PCB Tray Top.0004.ipt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]
2024-07-19 Made Printable Grate and Buoys 11 and 12
    Made a Printable Grate and Buoys 11 and 12. Updated Assembly, PCB spacers, and PCB tray. removed Plug as it is no longer needed.
    [Assembled Water Sensor Chassi.0007.iam, Assembled Water Sensor Chassi.0008.iam, Assembled Water Sensor Chassi.iam, Buoy 10 2in Sphere.0002.ipt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]
2024-07-20 Updated PCB tray, Printable Grate, and Water Sensor Cap
    [PCB tray CAD.0038.ipt, PCB tray CAD.0039.ipt, PCB tray CAD.ipt, Printable Grate.0001.ipt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]
2024-07-22 Added a V0.5.0 folder and reorganized files
    Updated the files to include a V0.5.0 folder and reorganized the files.
    [Arc Water Sensor.ipt, Assembled Water Sensor Chassi.iam, Battery for Water Sensor.ipt, Buoy 11 8inx1in shpere.ipt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]
2024-07-22 added STL files for printable parts
    [PCB Battery Tray.ipt, PCB Battery Tray.stl, PCB tray CAD.0042.ipt, PCB tray CAD.ipt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]
2024-07-28 Updated PCB tray, Assembly
    [Assembled Water Sensor Chassi.0010.iam, Assembled Water Sensor Chassi.iam, PCB Board.0002.ipt, PCB Board.ipt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]
2024-07-30 Shortened Pipe
    [Arc Water Sensor.ipt, Battery for Water Sensor.ipt, Connector and Hidnges.ipt, Hinge and Leaf Assembly.iam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]
2024-08-04 Gen Updates
    [Arc Water Sensor.ipt, Assembled Water Sensor Chassi.0010.iam, Battery for Water Sensor.ipt, Light Water Sensor.ipt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]
2024-08-08 Cad Model Updates and BOM
    [Arc Water Sensor.ipt, Assembled Water Sensor Chassi.0010.iam, Battery for Water Sensor.ipt, Light Water Sensor.ipt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]
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2024-11-05 replaced Amazon parts with eBay
    [PCB V0.6.3 BOM.xlsx]
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2025-02-10 MCU pin notation corrected.
    [PCB V0.6.3.kicad_sch, PCB tray CAD v2.3mf, PCB tray CAD v2.step]
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2025-05-30 V 0.5 PCB errors corrected
    [V0.5.0.kicad_pcb]
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2025-06-20 buoy version 15.5
    fixed some tolerances for the sink in m4 nuts, added a quality of life feature to help with assembly onto the pvc
    [buoy versio 15.5 clamshell with ibolt connection.ipt, buoy versio 15.5 clamshell with ibolt connection.stl]
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2025-06-20 slightly updated
    now wont give errors when sliced
    [buoy versio 15.7 clamshell no roof.0001.ipt, buoy versio 15.7 clamshell no roof.ipt, buoy versio 15.7.1 clamshell no roof.stl]
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2025-06-24 organizational fixes
    slight fix in organization
    [Bouy versioun 14 an stl file.stl, Bouy versioun 14 not an stl file.ipt, Buoy 11 8inx1in shpere.ipt, Buoy 11 8inx1in shpere.stl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]
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2025-06-25 edited bolt holes
    ensuring clearance
    [buoy version 16.5.1 edited eyeboltipt.dwg, buoy version 16.5.1 edited eyeboltipt.ipt]
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2025-07-29 buoy 17.0.5
    very slight fix; cleaned up buoy folder
    [buoy version 17.0.1dwg.stl, buoy version 17.0.1ipt.ipt, buoy version 17.0.2dwg.stl, buoy version 17.0.3.stl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]
2025-08-07 Intro work on shortening 0.5
    a bunch of new cad models for the assembly. Design of shortened 0.5 is incomplete for now.
    [0.5 short version assembly.0003.iam, 0.5 short version assembly.iam, Assembled Water Sensor Chassi.0010.iam, Assembled Water Sensor Chassi.0011.iam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]
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
